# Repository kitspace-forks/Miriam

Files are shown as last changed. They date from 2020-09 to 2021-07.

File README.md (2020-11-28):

Miriam
========



Miriam is an open-source instrument for isothermal amplification reactions such as LAMP and realtime fluorescence detection. The costs per instrument are below 1000 USD, and our goal is to make it less expensive, more robust, and ready for volume production. It could be used as part of a test for Covid-19 😷.

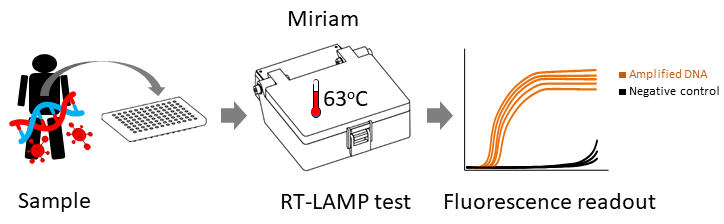
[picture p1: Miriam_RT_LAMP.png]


**🔥 Update 2020 Oct 15 🔥** Updates are coming. We have built and tested a Miriam device and will be updating this repository with details soon. In the meantime, the new [BOM list](PCB/BOM) of the Covid-19 adapted Miriam is updated constantly during our test.

## User guide ##

View the [Miriam User Guide](https://docs.google.com/document/d/1WqGBbrccB8vQHHecIBe8Pv8aZ-rZUhXWWKjNA4fbFT0/edit?usp=sharing) as a Google Doc. Comments and suggestions are welcome.

## Help wanted

Currently, we are seeking help testing and improving the device. If you have skills circuit board layout, product design, software engineering, user interface design,  and thermal simulation, we could use your help. Furthermore, if you would like to collaborate to put this instrument to real world use, please file an issue or contact [Andrew Straw](<straw@bio.uni-freiburg.de>).

## License



Copyright Miroculus Inc.2016
Based on original work from Arduino (Sweden)

This documentation describes Open Hardware and is licensed under the CERN OHL v. 1.2.

Licensed under CERN OHL v.1.2

You may redistribute and modify this documentation under the terms of the [CERN OHL v.1.2.](http://ohwr.org/cernohl). This documentation is distributed WITHOUT ANY EXPRESS OR IMPLIED WARRANTY, INCLUDING OF MERCHANTABILITY, SATISFACTORY QUALITY AND FITNESS FOR A PARTICULAR PURPOSE. Please see the CERN OHL v.1.2 for applicable conditions

## Introduction

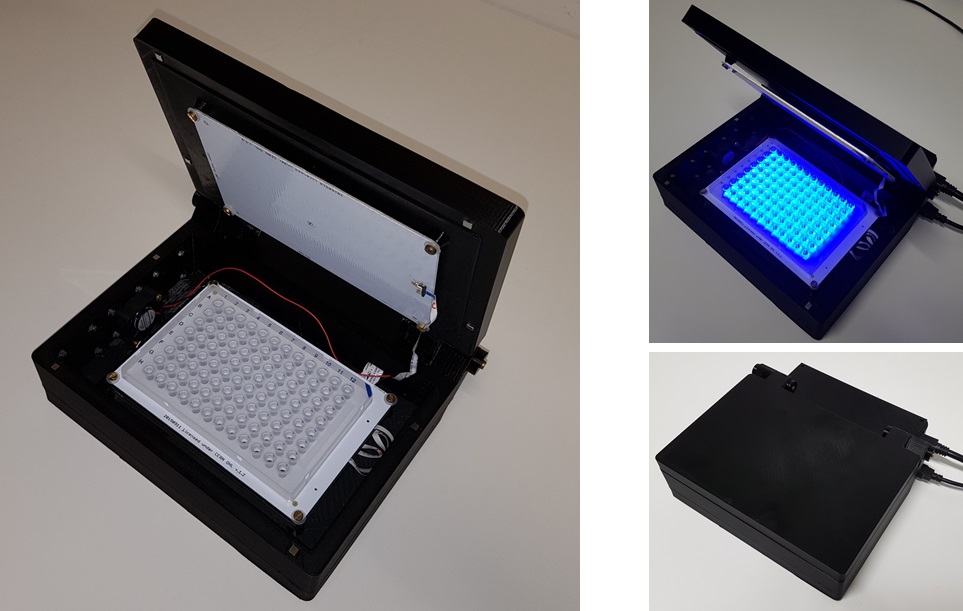
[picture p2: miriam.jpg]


Miriam is optimized for the Syto 9 fluorescent intercalating DNA dye. (The original design was for [calcein dye](http://loopamp.eiken.co.jp/e/products/fluore/index.html). The selected LED is an angle SMD led with peak wavelength 461nm. The photodiode is an RGB photodiode most sensitive to green light. The optics also include an emission filter utilized in theatrical lighting.  The development and selection of components is further described in a [Master's thesis](http://lutpub.lut.fi/handle/10024/159386) done from miriam. 

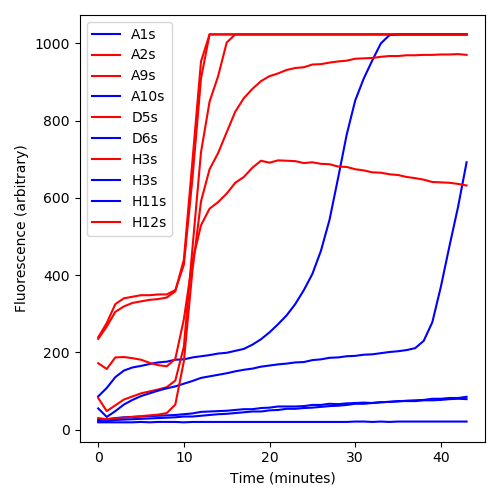
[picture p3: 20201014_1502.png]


**Figure 1.** LAMP reaction in 96 well plate. The reaction was performed in the center and corners of the 96 well plate to test heat uniformity.

In the performance testing of Miriam, the detection limit for DNA using LAMP as amplification platform has been 2amol in 10ul of sample (figure 1).



**Figure 2.** LAMP reaction with 2amol DNA input, fluorescence measured every 2 minutes (y, Normalized signal and x, cycle (2 min).

To report an issue, go to the [issues](http://github.com/strawlab/Miriam/issues) section

If you're interested in modifying or extending the Miriam platform, we strongly suggest you to send us an email discussing your ideas. That way you can coordinate with our team and others, giving your work a higher chance of being integrated into the official release.

## Design

The optics of Miriam plus are designed to support Syto9 + DNA. The emission and absorption spectra of Syto9 + DNA are represented in Figure 3.

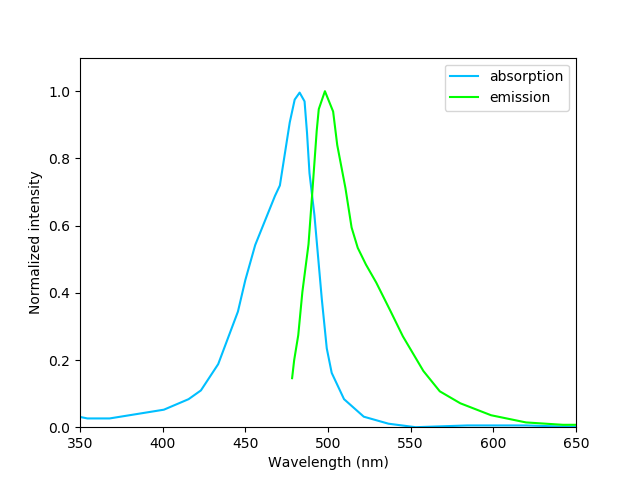
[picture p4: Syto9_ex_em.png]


**Figure 3.** Syto9+DNA emission and excitation spectra.

LEE filter 738 is used for blocking the excitation light. Whole optic design of Miriam plus is shown in Figure 4.

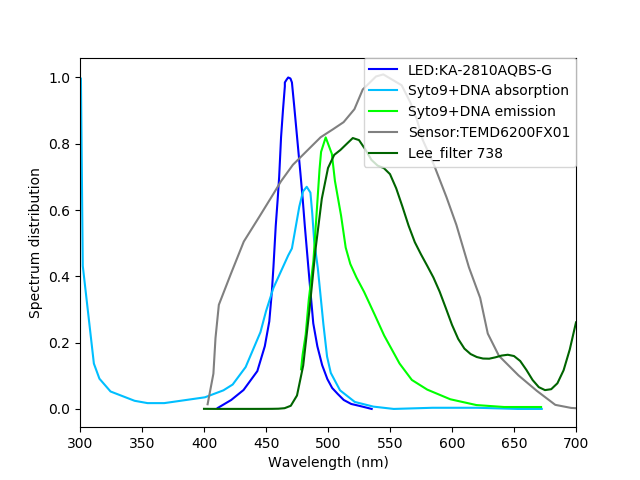
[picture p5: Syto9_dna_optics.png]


**Figure 4.** Optic design for Miriam plus to detect Syto9 + DNA.

The middle heating board and the LED and PD arrangements have been designed to support 96-well plates with the following dimensions (figure 5).



**Figure 5.** 96-well plate dimensions supported by Miriam

To control the heating of Miriam there are two heater PCBs. They have been designed so that in the middle is a 10 kohm SMD thermistor and the heat is generated by current flowing through the copper traces. These traces have been designed to be so long and narrow that they create an internal resistance of few ohms. The traces are closer to each other in the edges because heat is measured from the middle and the edges of the PCB boards meet ambient air and they need to produce more heat. (Figure 6.)

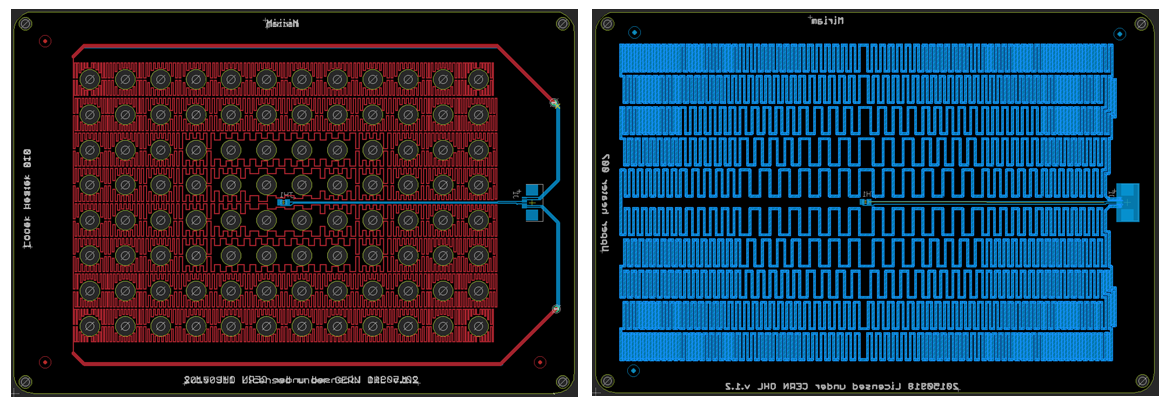
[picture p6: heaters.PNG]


**Figure 6.** Heating plates, heat is generated by trace resistance. Right: The middle heater creating the temperature required for amplification (58-68 degrees C). Left: The top heater keeping vapor from condensing to the lid, kept at 80 degrees C. 

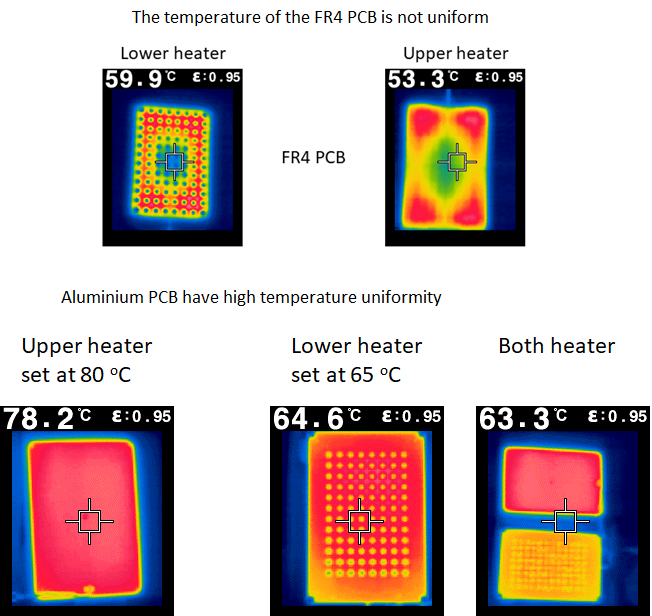
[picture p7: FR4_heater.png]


**Figure 6a.** The distribution of heat in the FR4 and Al heaters. FR4 heaters may work with small number of wells setup. For Miriam, we recommend using Al boards for better heat distribution.

Original Miriam design has 2.5 oC difference in temperature of the central wells and those on the far edge. Adding a heating wire on the edge of the lower heater can improve the uniformity (Fig. 6b). The temperature difference is reduced as low as 1oC or +/-0.5 oC by tuning the heat wire temperature (current) manually. An additional close-loop control for the heating wire would further improve the temperature uniformity.    
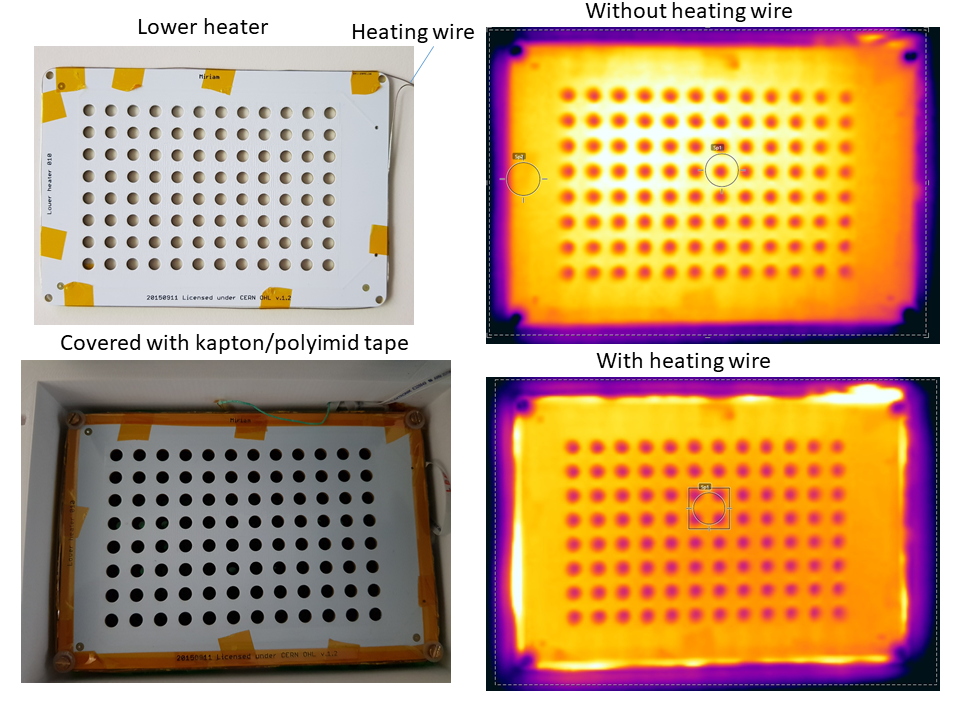
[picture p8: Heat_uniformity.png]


**Figure 6b.** Additional heat wire (left) helps to improve heat uniformity of the plate as in thermography images(right).

The heat uniformity of Miriam would be improved further by optimizing the heating traces of the heaters. Using a PCB thermal analysis software (Fig. 6C) with certain protocol for heat trace optimization would help to boost the design process.

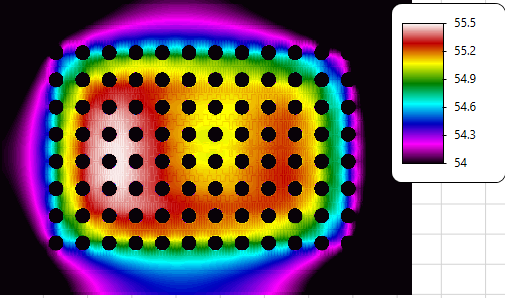
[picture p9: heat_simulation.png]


**Figure 6c.** Heat distribution of the lower heater obtained from PCB thermal analysis software [(More detail of the analysis)](https://www.adam-research.de/en/2020/10/corona-forschung-mit-trm3/).

The detection of fluorescence is done with 96 LEDs and 96 photodiodes creating LED and photodiode PCBs. The LED peak wavelength is 470 nm and photodiode is a green RGB photodiode. The measured voltage is amplified with an operational amplifier to 0-5 V that is then converted by Arduino’s 8-bit ADC to be a numerical value. (figure 7.)

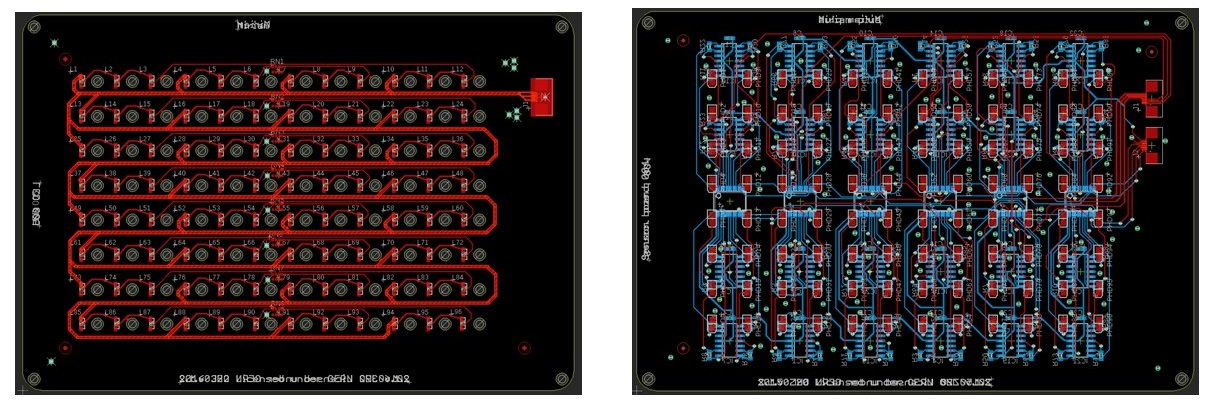
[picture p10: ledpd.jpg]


**Figure 7.** LED (left) and new photodiode (right) PCBs.

All of these boards are controlled by a shield that is directly mounted to the Arduino mega board (figure 8). The shield contains three MOSFETs to control LED board and the two heater boards, the required components to read the heat from the thermistors as well as a WIFI chip. The WIFI chip makes it possible for Arduino to be connected to a local WIFI and this way communicate autonomously to a web service.

shield

**Figure 8.** The Arduino shield. 

Assembly
------------
3D print the printable parts under folder ["3D model"](3D%20Model), sand them if nescessary to make them align with each other. Assemble the boards as presented in the Figure 9. In the assembly cut with scissors the emission filter and glue to the filter holder.

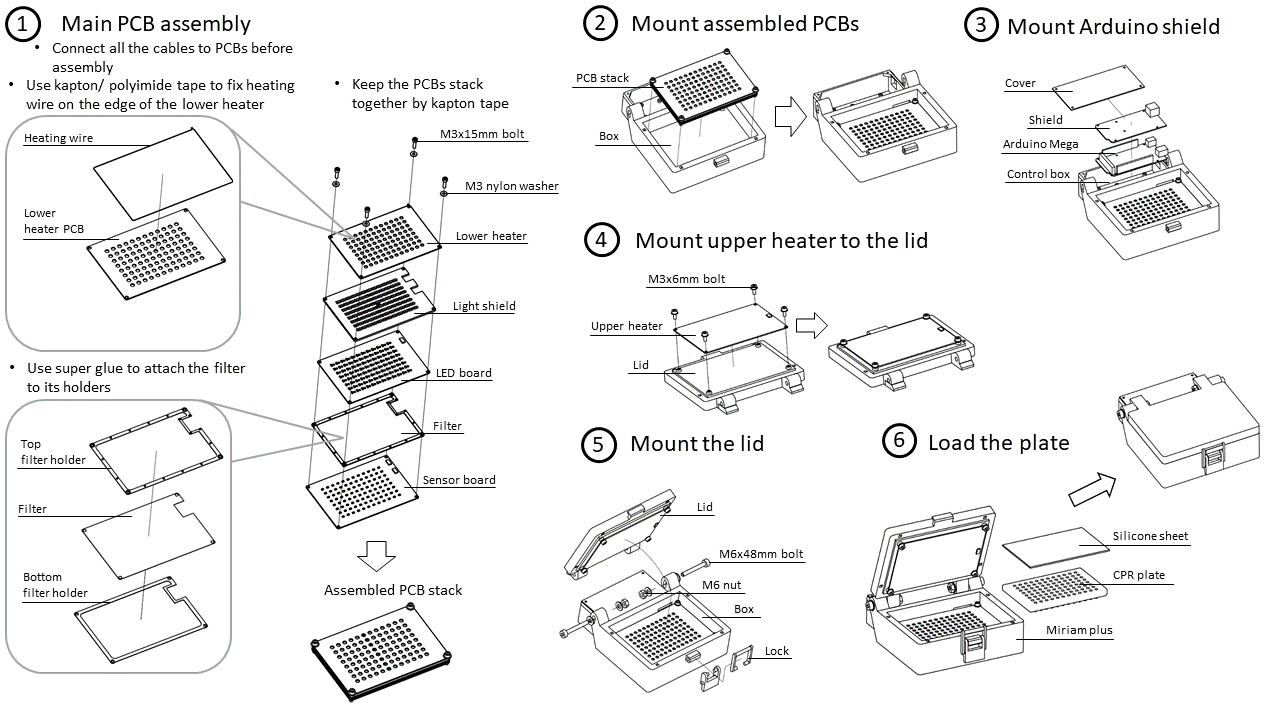
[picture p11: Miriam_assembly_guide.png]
screws


**Figure 9.** Miriam assembly instruction. [High resolution version for printing](Miriam_assembly_guide.pdf) and [Video](https://youtu.be/ynIIGh6IMBA)

**Note:** All the cables used for Miriam must be "Opposite Side Contacts".
          For hand soldering, it is recommended to use solder paste and stencils for the sensor board. If it is possible, use reflow oven for the bottom side.
          
**Updated components:** The new [BOM list](PCB/BOM) of the Covid-19 adapted Miriam will be updated constantly during our test.

Software
------------
We just tested and improved the serial version of the software [Serial_003](Programs/Serial_003).

Improvement wish list
------------
A more robust type of connector can be considered. May change to 1mm pitch. 
Optimization for the traces of lower heater board to have uniformity heat distribution.

Credits
--------
The original Miriam is an open source project, supported by Miroculus in collaboration with Arduino (Sweden). The team was led by Juho Terrijarvi.

This version of Miriam has been improved by [Straw Lab](https://strawlab.org) to make it work with Syto-9 + DNA for potentially Covid-19 test.
Icon and image designed by Miroculus.

The PCB thermal analysis is performed by [ADAM research](https://www.adam-research.de/en/). 

Code of conduct
--------
Anyone who interacts with this software in any space, including but not limited
to this GitHub repository, must follow our [code of
conduct](code_of_conduct.md).

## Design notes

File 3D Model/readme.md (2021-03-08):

# 3D printable parts

Miriam box is composed of 3D printed parts. It is designed to fit the bed of Prusa i3 mk3 printer.
Printer setting is: PETG with 20% cubic infill, 200% speed.

**Attention!!!** If you need to use melting curve, please use ABS for printing the box.

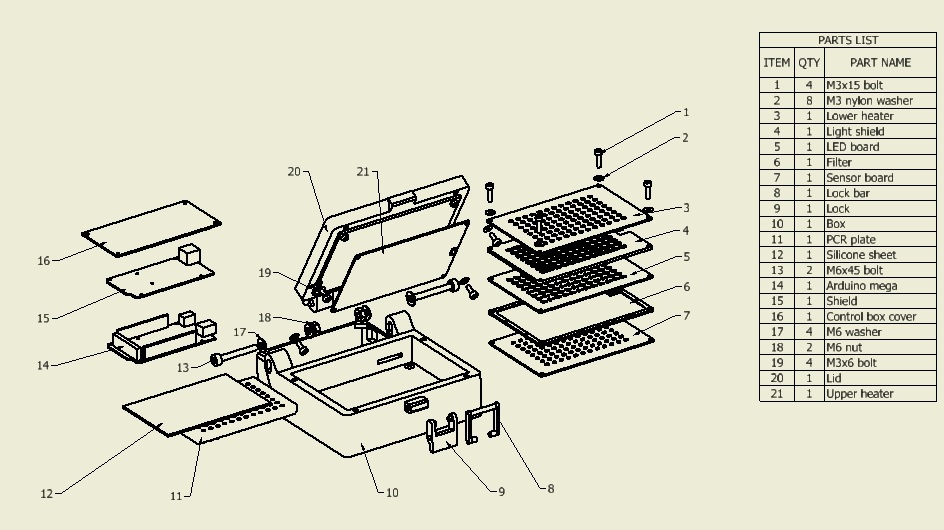
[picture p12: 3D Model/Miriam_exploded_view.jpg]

Exploded view with part list of Miriam. [High resolution version for printing](Miriam_exploded_view.pdf)

## [box.stl](box.stl)

Box is where the mid heating and optic PCBs are located and where the plate to run the assay comes to. It also houses the Arduino Mega and its control shield in the back of the case. 

The outer dimensions of the base are 203 x 173 x 49 mm.

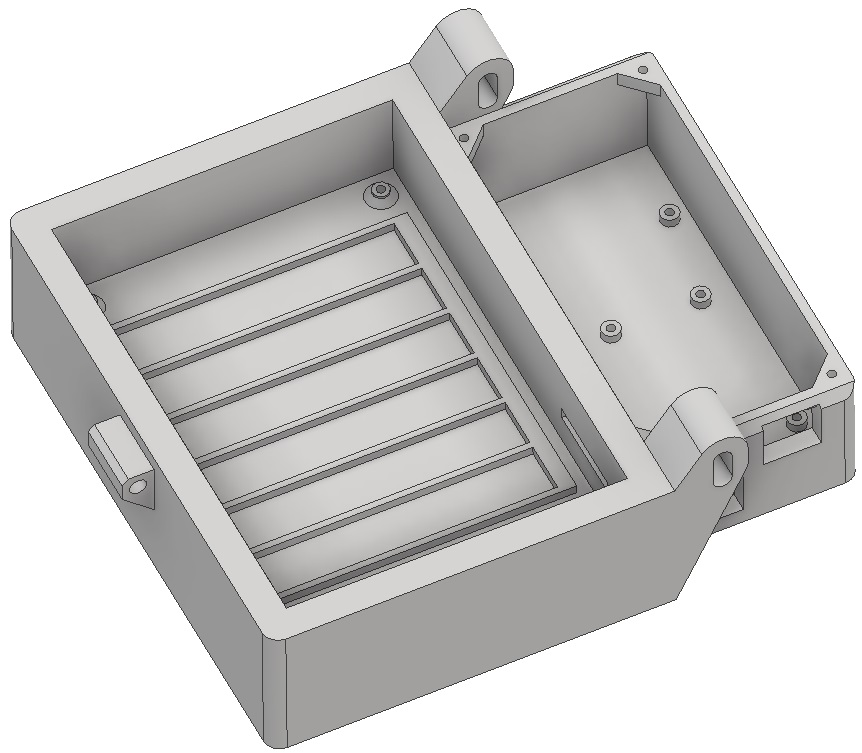
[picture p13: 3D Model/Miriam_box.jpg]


## [lid.stl](lid.stl)

This lid is meant to cover the box and house the upper heating board. The outer dimensions are 165 x 173 x 21 mm.

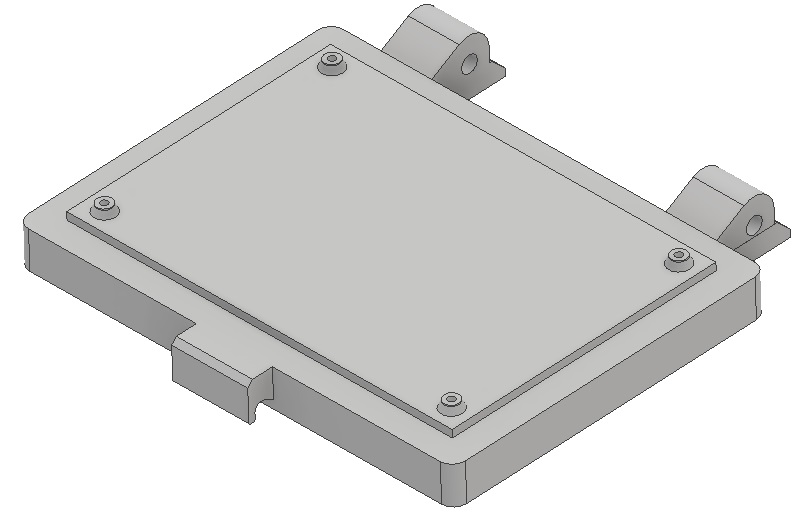
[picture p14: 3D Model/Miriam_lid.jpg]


## [control_cover.stl](control_cover.stl)

Cover is meant to hide the Arduino mega and shield in the back of the case. 

## [filter_holder_bottom.stl](filter_holder_bottom.stl) and [filter_holder_top.stl](filter_holder_top.stl)

Cut the filter and glue it in the middle of these two filters. The bottom one is toward the sensor board.

## [lock.stl](lock.stl) and [lock_bar_new.stl](lock_bar_new.stl)

The lock is meant to tighten the lid during testing.

## [pw_stop_2mm.stl](pw_stop_2mm.stl)

The stopper for the power plug to avoid it to go all the way

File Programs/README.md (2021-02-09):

Miriam SW/FW
========

(c) 2016 Juho Terrijarvi juho@miroculus.com, Miroculus Inc.

(c) 2014 Juanjo Tara j.tara@arduino.cc, Arduino Verkstad AB (For FWs)

These programs are free software: you can redistribute them and/or modify them under the terms of the GNU General Public License as published by the Free Software Foundation, either version 3 of the License, or (at your option) any later version.

These programs are distributed in the hope that they will be useful, but WITHOUT ANY WARRANTY; without even the implied warranty of MERCHANTABILITY or FITNESS FOR A PARTICULAR PURPOSE.  See the GNU General Public License for more details.

You should have received a copy of the GNU General Public License along with this program.  If not, see <http://www.gnu.org/licenses/>.

## Programs

Firmware is written with [Arduino IDE](https://www.arduino.cc/en/main/software) and the software with Visual Studio 2015 open community using C#.

* Serial_003 is meant for communication between computer and Miriam via USB cable and string messages

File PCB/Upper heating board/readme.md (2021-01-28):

# UH_007

- 1 layer PCB
- One sided assembly
- material Aluminium
- 1oz copper
- 1.6 mm thick
- Leadfree HAL
- Black soldermask
- White silkscreen

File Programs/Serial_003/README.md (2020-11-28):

Serial_003
========

This SW / FW combination is meant for serial communication between a computer and Miriam. Miriam is connected with a USB cable to the controlling computer and messaging between the two happen via string messages over RX/TX protocol.
- SW 'R' (read assay) - FW 'A11,A12,...A1,A2, B11,B12,...,B1,B2, ..., E2'
- SW 'i' (info) - FW 'outputMiddle, outputUpper, temperatureUpper, temperatureMiddle, temperatureUpperC, temperatureMiddleC, outputExtra, temperatureExtra, termperatureBox, temperatureExtraC, temperatureBoxC'
- SW 'U param' (upper wanted temperature, i.e. U 80) - FW 'temperatureUpperSet'
- SW 'M param' (middle wanted temperature, i.e. M 63) - FW 'temperatureMiddleSet'
- SW 'E param' (extra wanted temperature, i.e. E 63) - FW 'temperatureExtraSet'
- SW 'T param' (box temperature threshold, i.e. T 45) - FW 'temperatureBoxThrSet'
- SW 'H' (heat boards) - FW 'Heating boards' 
- SW 'C' (cancel, turn off the heat) - FW 'Cancel'
- SW 'l' (turn on status LED) - FW 'Status LED on'
- SW 'o' (turn off status LED) - FW 'Status LED off'

Once the temperature has been set, the actual temperature needs to be refreshed by clicking 'Ask heat'. The assay, once started, can always be turned off simply by closing the program. The assay results are saved to the desktop in a .csv file.

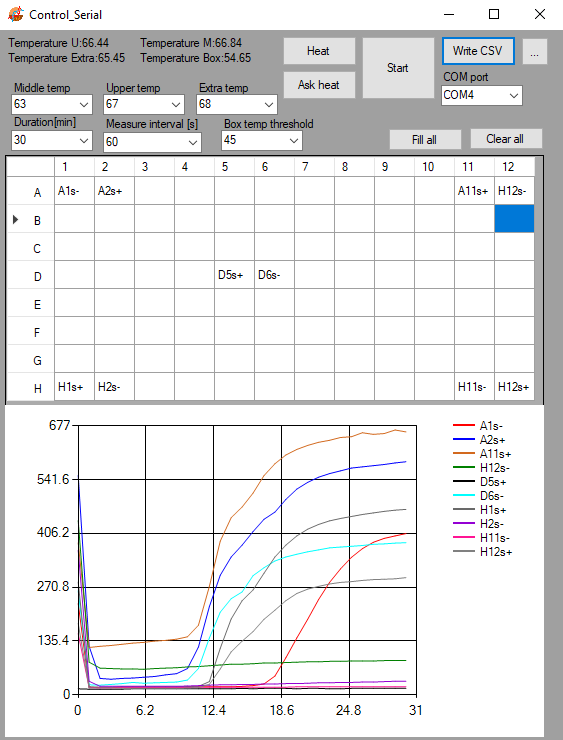
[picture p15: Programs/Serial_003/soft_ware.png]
screws


**Figure 1.** User interface of Serial_003.

Temperature U: measured temperature of the upper heater.

Temperature M: measured temperature of the lower heater.

Temperature Extra: measured temperature of the extra heater (wire).

Temperature Box: measured temperature of the box.

Middle temp: set temperature of the lower heater.

Upper temp: set temperature of the upper heater.

Extra temp: set temperature of the upper heater.

Box threshold: set designed temperature of the box for preheating.

Duration: Total reaction time in minute. After this period, the heaters and sensor readout will stop.

Measure interval: the interval in seconds between two readouts. Minimum value is 11s. For real time measurement, it is recommended to set the interval not lower than 60s as the resistors of the LED board can produce additional heat to the wells in the central collumns. 

COM port: choose your device.

[Heat]: Start heating program.

[Ask heat]: Check the temperature of the heaters and update on the UI.

[Start]: Start the readout cycle as defined by "Duration" and "Measure interval".

[Write CSV]: Save data to CSV.

[...]: Choose folder for saving data.

[Fill all]: Auto name the wells as their positions.

[Clear all]: clear the well name.

**Note:**

The program saves the temperature of the heaters and sensor readouts of all the wells but only plot on the UI those with name filled.

It is recommended to preheat the device at the desired temperature for 30 min before loading the samples.

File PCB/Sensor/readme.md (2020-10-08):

# Sensor_004
- Changed the order of power pins of the connector and the new footprint for new photodiode (TEMD6200FX01)

- material FR4
- 2 layer
- double sided assembly
- 1oz copper
- 1.6 mm thick
- Leadfree HAL
- Black soldermask
- White silkscreen

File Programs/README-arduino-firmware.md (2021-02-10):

# Arduino firmware for Miriam

This requires the [Arduino software](https://www.arduino.cc/en/Guide/Windows).

* `Serial_003` - this contains the source code ("sketch") for the Arduino
  firmware in the file `Serial_003.ino`.
* `PID_v1.zip` - this is a library for Arduino.

## Installing

1. The `PID_v1` library should be installed in the Arduino IDE [according to
   these instructions](https://www.arduino.cc/en/guide/libraries). Follow the
   "Importing a .zip Library" section and select `PID_v1.zip`.

2. In the Arduino IDE, go to "Tools > Board" then select `Arduino Mega or Mega
   2560`.

3. In the Arduino IDE, select the port to the Arduino device. Go to "Tools >
   Port" then select the correct port, which depends on your computer.

4. Then the sketch can then be uploaded using the IDE. [Here is a tutorial about
   getting started with Arduino](https://www.arduino.cc/en/main/howto).

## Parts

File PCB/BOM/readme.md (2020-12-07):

# Components

Components required for the PCB assembly are listed in the BOM files in this
directory. Each .xlsx file contains link to the individual components.

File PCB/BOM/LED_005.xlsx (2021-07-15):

PCB: | LED_003
References | pcs/pcb | Value | Package | Description | Remark | Link
RN1,RN2,RN3,RN4,RN5,RN6,RN7,RN8 | 8 | 181 | CAY16 | Array Chip Resistor | 4R-NCAY16 | https://de.farnell.com/bourns/cat16-181j4lf/widerst-netzwerk-isol-180r-0-063w/dp/2908145
FD1,FD2,FD3 | 3 | FIDUCIALMOUNT | FIDUCIA-MOUNT | FIDUCIALMOUNT
L1,L2,L3,L4,L5,L6,L7,L8,L9,L10,L11,L12,L13,L14,L15,L16,L17,L18,L19,L20,L21,L22,L23,L24,L25,L26,L27,L28,L29,L30,L31,L32,L33,L34,L35,L36,L37,L38,L39,L40,L41,L42,L43,L44,L45,L46,L47,L48,L49,L50,L51,L52,L53,L54,L55,L56,L57,L58,L59,L60,L61,L62,L63,L64,L65,L66,L67,L68,L69,L70,L71,L72,L73,L74,L75,L76,L77,L78,L79,L80,L81,L82,L83,L84,L85,L86,L87,L88,L89,L90,L91,L92,L93,L94,L95,L96 | 96 | KA-2810AQBS-G | LED_0.2 | LED_0.2 | LED | https://de.farnell.com/kingbright/ka-2810aqbs-g/led-smd-2-8x0-8mm-seitl-abstr/dp/2146478
J1 | 1 |  | 68710614522 | WE-FPC 0.5mm SMT ZIF Horizontal Bottom Contact, 6 Pins=>Code : Con_FPC_ZIF_0.50_68710614522 |  | https://de.farnell.com/wurth-elektronik/68710614522/ffc-05mm-90-unten-ziif-6kont/dp/1641913

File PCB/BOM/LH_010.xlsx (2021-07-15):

PCB: | LH_010
References | pcs/pcb | Value | Package | Description | Remark | Link
J1 | 1 |  | 68710614522 | WE-FPC 0.5mm SMT ZIF Horizontal Bottom Contact, 6 Pins=>Code : Con_FPC_ZIF_0.50_68710614522 |  | https://de.farnell.com/wurth-elektronik/68710614522/ffc-05mm-90-unten-ziif-6kont/dp/1641913
TH1 | 1 | 10K | THERMISTOR_SMD_0603 | NTCS0603E3103FLT | NTC | https://www.mouser.de/ProductDetail/594-NTCS0603E3103FLT

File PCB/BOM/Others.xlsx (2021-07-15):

PCB: | UH_007
References | pcs/pcb | Value | Package | Description | Remark | Link
C1, C2 | 2 | 10u | A/3216-18R | POLARIZED CAPACITOR, European symbol |  | https://www.mouser.de/ProductDetail/KEMET/T495A106K010ATA2K0?qs=ds50AKTGxA9fL71AH2RCoQ%3D%3D
TH1, TH2 | 2 | 10K | NTCS0603E3103FLT | THERMISTOR_SMD_0603 | NTC
R1, R2 | 2 | 10k | 0603
Filter | 1 | 738 |  | LEE Filter-Bogen Nr. 738 Jas Green |  | https://www.castinfo.de/produkte/filterfolien/filterfolien/lee-filter-bogen-nr-738-jas-green.html
Power input | 1 | 12V, 10A | ALM120PS12 | External power supply |  | https://de.rs-online.com/web/p/products/1720772/
Thermal Gap Filler Pad | 1 |  | 40001020 |  |  | https://www.mouser.de/ProductDetail/710-40001020
Cable | 5 | 0,5 mm pitch | 687706200002 | opposite side contacts |  | https://www.mouser.de/ProductDetail/710-687706200002
Heating wire |  | RD 100/0,3 |  | Block RD 100/0,3 Widerstandsdraht 6.93 Ω/m 158 m |  | https://www.conrad.de/de/p/block-rd-100-0-3-widerstandsdraht-6-93-m-158-m-422450.html
Arduino Mega 2560 |  |  |  |  |  | https://www.mouser.de/ProductDetail/782-A000067

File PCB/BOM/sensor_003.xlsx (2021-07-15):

PCB: | sensor_002
References | pcs/pcb | Value | Package | Description | Remark | Link
C1,C2,C3,C4,C5,C6,C7,C8,C9,C10,C11,C12,C13,C14,C15,C16,C17,C18,C19,C20,C21,C22,C23,C25 | 24 | 100nF | C0603 | C-EUC0603 | CAPACITOR, European symbol
R1,R2,R3,R4,R5,R7,R8,R9,R10,R11,R12,R13,R14,R15,R16,R17,R18,R19,R20,R21,R22,R23,R24,R25,R26,R27,R28,R29,R30,R31,R32,R33,R34,R35,R36,R37,R38,R39,R40,R41,R42,R43,R44,R45,R46,R47,R48,R49,R50,R51,R52,R53,R54,R55,R56,R57,R58,R59,R60,R61,R62,R63,R64,R65,R66,R67,R68,R69,R70,R71,R72,R73,R74,R75,R76,R77,R78,R79,R80,R81,R82,R83,R84,R85,R86,R87,R88,R89,R90,R91,R92,R93,R94,R95,R96,R97 | 96 | 100Mohm | R0603 | R-EU_R0603 | RESISTOR, European symbol
U1,U2,U3,U4,U5,U6 | 6 | 74HC4067 | SSOP24 | MUX-1X16 | 1x16 Channel Analog Multiplexer/Demultiplexer [Part No.] | https://www.mouser.de/ProductDetail/595-CD74HC4067SM96G4
PHD1,PHD2,PHD3,PHD4,PHD5,PHD6,PHD7,PHD8,PHD9,PHD10,PHD11,PHD12,PHD13,PHD14,PHD15,PHD16,PHD17,PHD18,PHD19,PHD20,PHD21,PHD22,PHD23,PHD24,PHD25,PHD26,PHD27,PHD28,PHD29,PHD30,PHD31,PHD32,PHD33,PHD34,PHD35,PHD36,PHD37,PHD38,PHD39,PHD40,PHD41,PHD42,PHD43,PHD44,PHD45,PHD46,PHD47,PHD48,PHD49,PHD50,PHD51,PHD52,PHD53,PHD54,PHD55,PHD56,PHD57,PHD58,PHD59,PHD60,PHD61,PHD62,PHD63,PHD64,PHD65,PHD66,PHD67,PHD68,PHD69,PHD70,PHD71,PHD72,PHD73,PHD74,PHD75,PHD76,PHD77,PHD78,PHD79,PHD80,PHD81,PHD82,PHD83,PHD84,PHD85,PHD86,PHD87,PHD88,PHD89,PHD90,PHD91,PHD92,PHD93,PHD94,PHD95,PHD96 | 96 | TEMD6200FX01 | PD_0.2 | PD_0.2 | Photodiode | https://www.mouser.de/ProductDetail/782-TEMD6200FX01
FD1,FD2,FD3,FD4,FD5,FD6 | 6 | FIDUCIALMOUNT | FIDUCIALMOUNT | FIDUCIA-MOUNT
IC1,IC2,IC3,IC4,IC5,IC6,IC7,IC8,IC9,IC10,IC11,IC12,IC13,IC14,IC15,IC16,IC17,IC18,IC19,IC20,IC21,IC22,IC23,IC24 | 24 | LMV324 | SO14 |  | OP AMP | https://www.mouser.de/ProductDetail/511-LMV324LIDT
J1, J2 | 2 |  | 68710614522 | WE-FPC 0.5mm SMT ZIF Horizontal Bottom Contact, 6 Pins=>Code : Con_FPC_ZIF_0.50_68710614522 |  | https://de.farnell.com/wurth-elektronik/68710614522/ffc-05mm-90-unten-ziif-6kont/dp/1641913

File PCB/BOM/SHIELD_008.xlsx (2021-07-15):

PCB: | SHIELD_008
References | pcs/pcb | Value | Package | Description | Remark | Link
R7 | 1 | 1.69k | R0603 | RESISTOR, European symbol
R3, R4, R8, R16 | 4 | 100R | R0603 | RESISTOR, European symbol
C2, C5, C7 | 3 | 100n | C0603 | CAPACITOR, European symbol
R1, R2, R5, R6, R9, R13, R14, R15, R17 | 9 | 10K | R0603 | RESISTOR, European symbol
C3, C4 | 2 | 10u | A/3216-18R | POLARIZED CAPACITOR, European symbol |  | https://www.mouser.de/ProductDetail/80-T495A106K10ATA2K0
JP7 | 1 | 10x1F-H8.5 | 1X10 | PIN HEADER
JP5 | 1 | 18x2F-H8.5 | 2X18 | PIN HEADER
J6 | 1 | 22-23-2021 | 22-23-2021 | .100 (2.54mm) Center Header - 2 Pin"
R10 | 1 | 3.3k | R0603 | RESISTOR, European symbol
R11, R12 | 2 | 4.12k | R0603 | RESISTOR, European symbol
C1, PC1, PC2 | 3 | 47u | PANASONIC_D | POLARIZED CAPACITOR, European symbol |  | https://www.mouser.de/ProductDetail/647-UWX0J470MCL1
JP1, JP2, JP3, JP4, JP6 | 5 | 8x1F-H8.5 | 1X08 | PIN HEADER
IC1, IC2, IC3, IC6 | 4 | PSMN017-30BL,118 | PSMN017-30BL,118 | N-Channel PowerTrench MOSFET |  | https://www.mouser.de/ProductDetail/771-PSMN017-30BL%2c118
WIFI | 1 | ESP12 | ESP12 | ESP8266 Wifi module 12 |  | https://www.mouser.de/ProductDetail/485-2491
D1, D2 | 2 | S1AB-13-F | S1AB-13-F | DIODE |  | https://www.mouser.de/ProductDetail/621-S1AB-F
F1 | 1 | MF-R1100 | LITTLEFUSE | LITTLEFUSE |  | https://www.mouser.de/ProductDetail/652-MF-R1100
IC4 | 1 | NCV1117ST50T3GOSCT-ND | SOT223 | Adjustable Output Low Dropout Voltage Regulator 800 mA |  | https://www.mouser.de/ProductDetail/863-NCV1117ST50T3G
IC5 | 1 | NCV1117ST33T3GOSCT-ND |  | Adjustable Output Low Dropout Voltage Regulator 800 mA |  | https://www.mouser.de/ProductDetail/863-NCV1117ST33T3G
D3, D4, D5, D6 | 4 | RGL34G-E3/98 | RGL34G-E3/98 | Semiconductor diode |  | https://de.farnell.com/vishay/rgl34g-e3-98/diode-fast-0-5a-400v-smd/dp/1336528?st=RGL34G-E3/98
J7 | 1 | KPJX-4S-S | KPJX-4S-S | 4 _Power_ Position Circular Connector Jack, Female Sockets Solder |  | https://www.mouser.de/ProductDetail/806-KPJX-4S-S
J1, J2, J3, J4, J5 | 5 |  | 68710614522 | WE-FPC 0.5mm SMT ZIF Horizontal Bottom Contact, 6 Pins=>Code : Con_FPC_ZIF_0.50_68710614522 |  | https://de.farnell.com/wurth-elektronik/68710614522/ffc-05mm-90-unten-ziif-6kont/dp/1641913

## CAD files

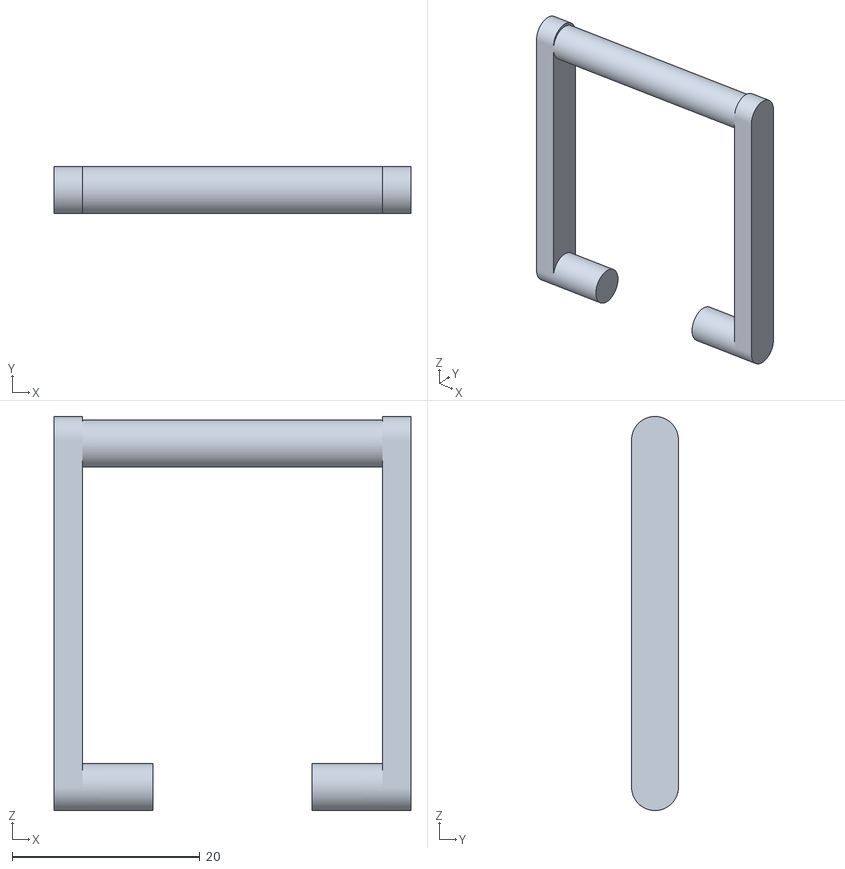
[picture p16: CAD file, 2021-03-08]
3D Model/lock_bar_new.stl
38.0 x 5.00 x 42.0

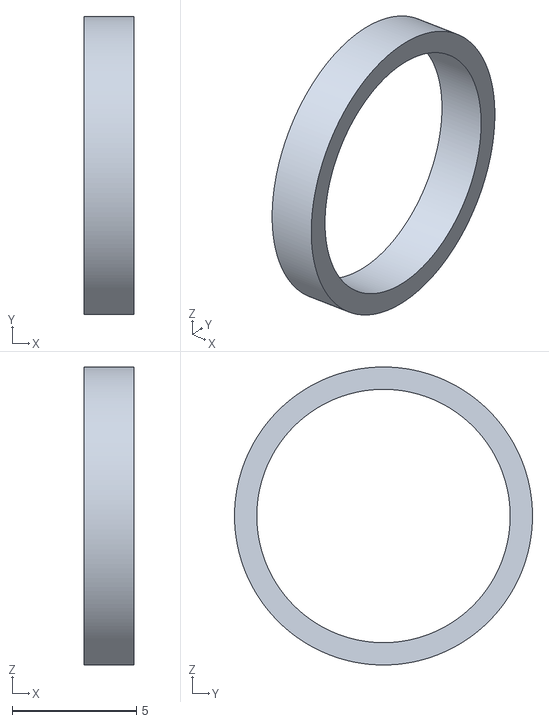
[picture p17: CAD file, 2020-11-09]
3D Model/pw_stop_2mm.stl
2.00 x 12.0 x 12.0

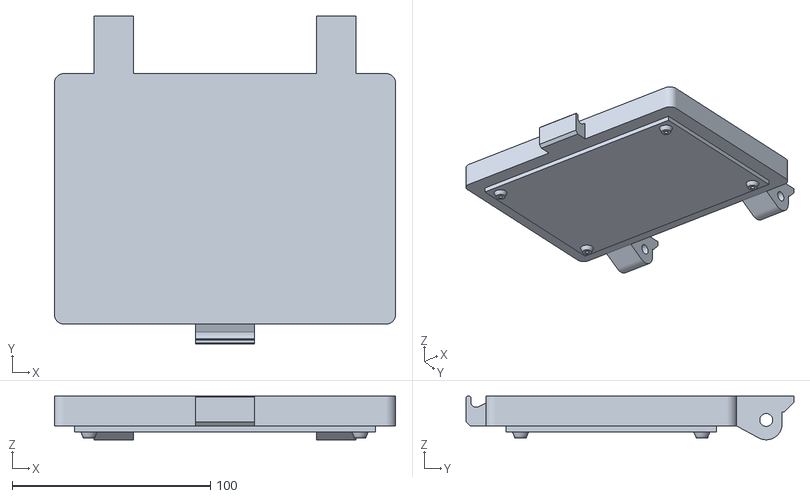
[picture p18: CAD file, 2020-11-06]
3D Model/lid.stl
172.3 x 165.5 x 22.0

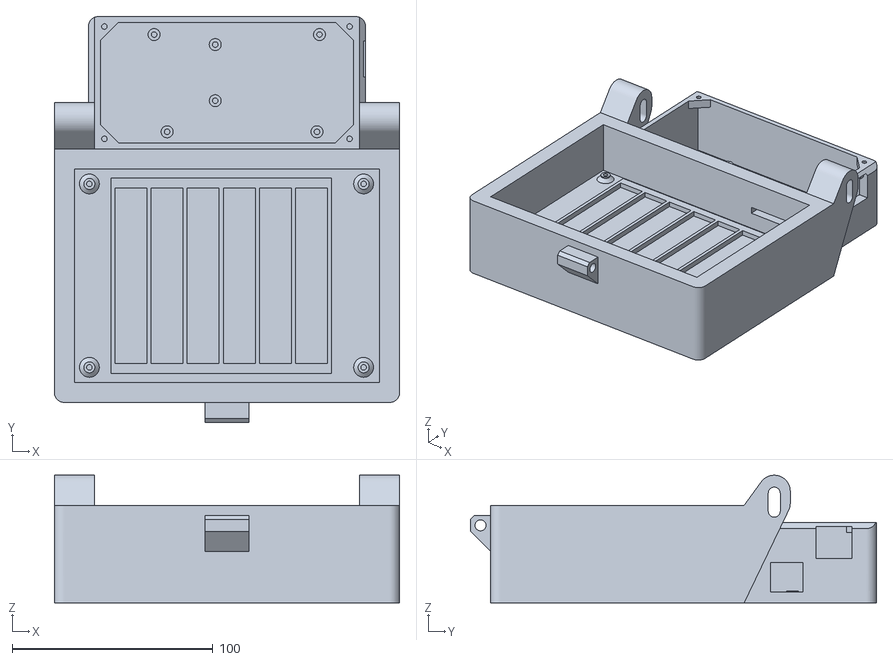
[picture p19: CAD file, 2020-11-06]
3D Model/box.stl
172.3 x 202.5 x 63.6

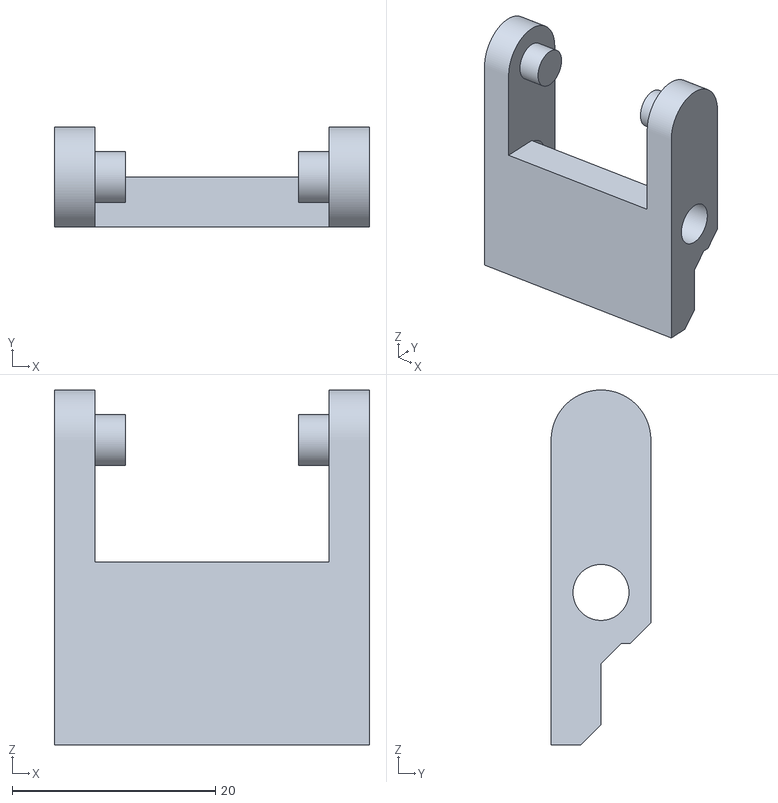
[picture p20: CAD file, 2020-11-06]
3D Model/lock.stl
31.0 x 9.80 x 34.9

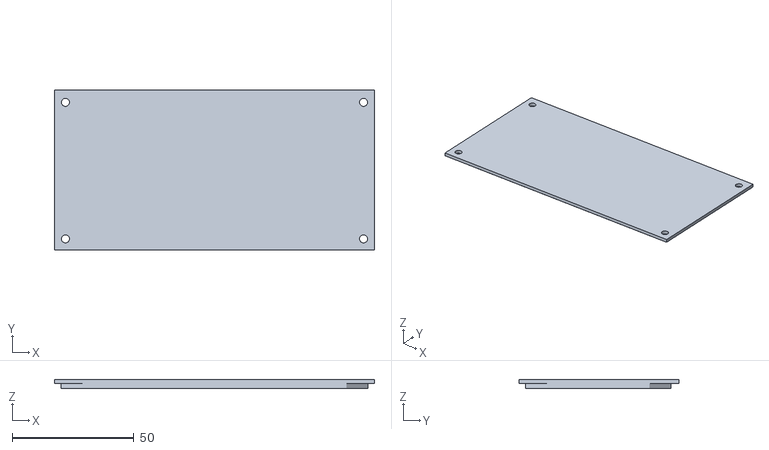
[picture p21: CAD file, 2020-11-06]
3D Model/control_cover.stl
131.3 x 65.5 x 3.50

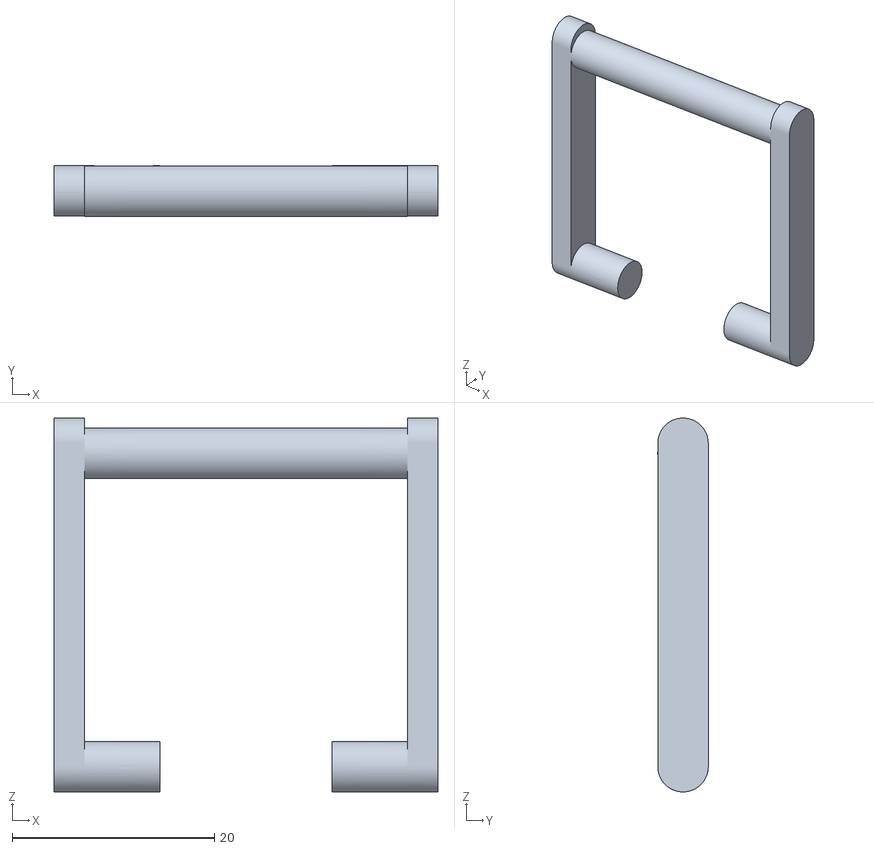
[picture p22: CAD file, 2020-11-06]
3D Model/lock_bar.stl
38.0 x 5.00 x 37.0

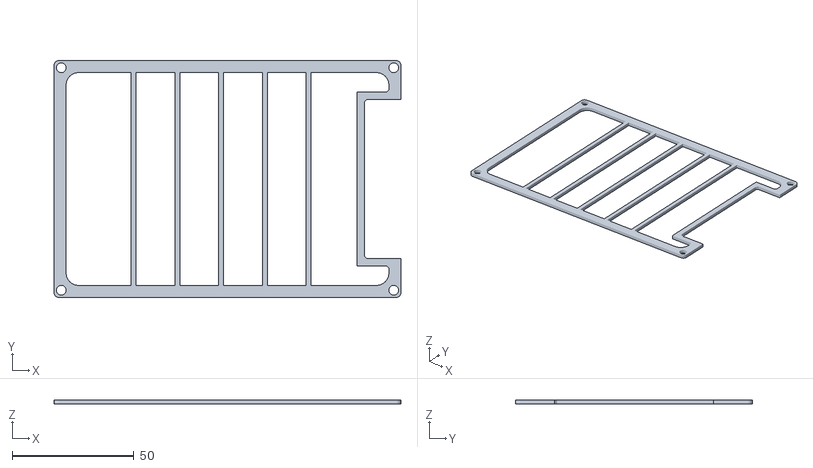
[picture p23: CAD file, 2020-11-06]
3D Model/filter_holder_top.stl
142.8 x 97.5 x 1.80

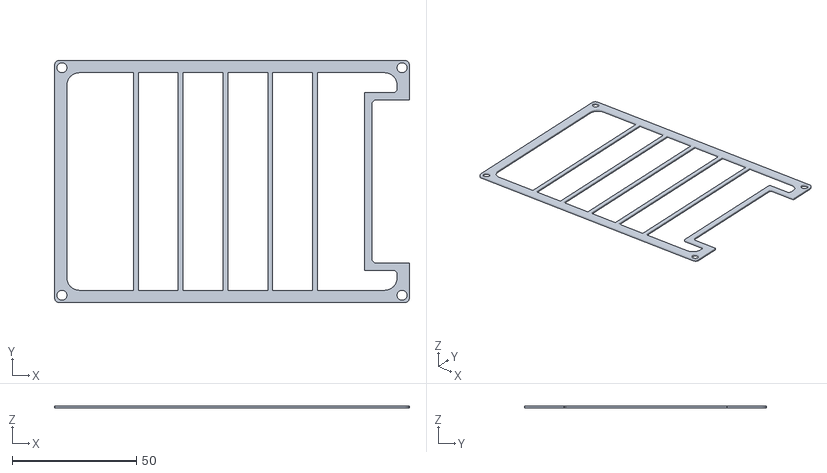
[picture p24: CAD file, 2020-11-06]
3D Model/filter_holder_bottom.stl
142.8 x 97.5 x 1.00

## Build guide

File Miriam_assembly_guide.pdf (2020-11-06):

# 1 Main PCB assembly

# 2 Mount assembled PCBs

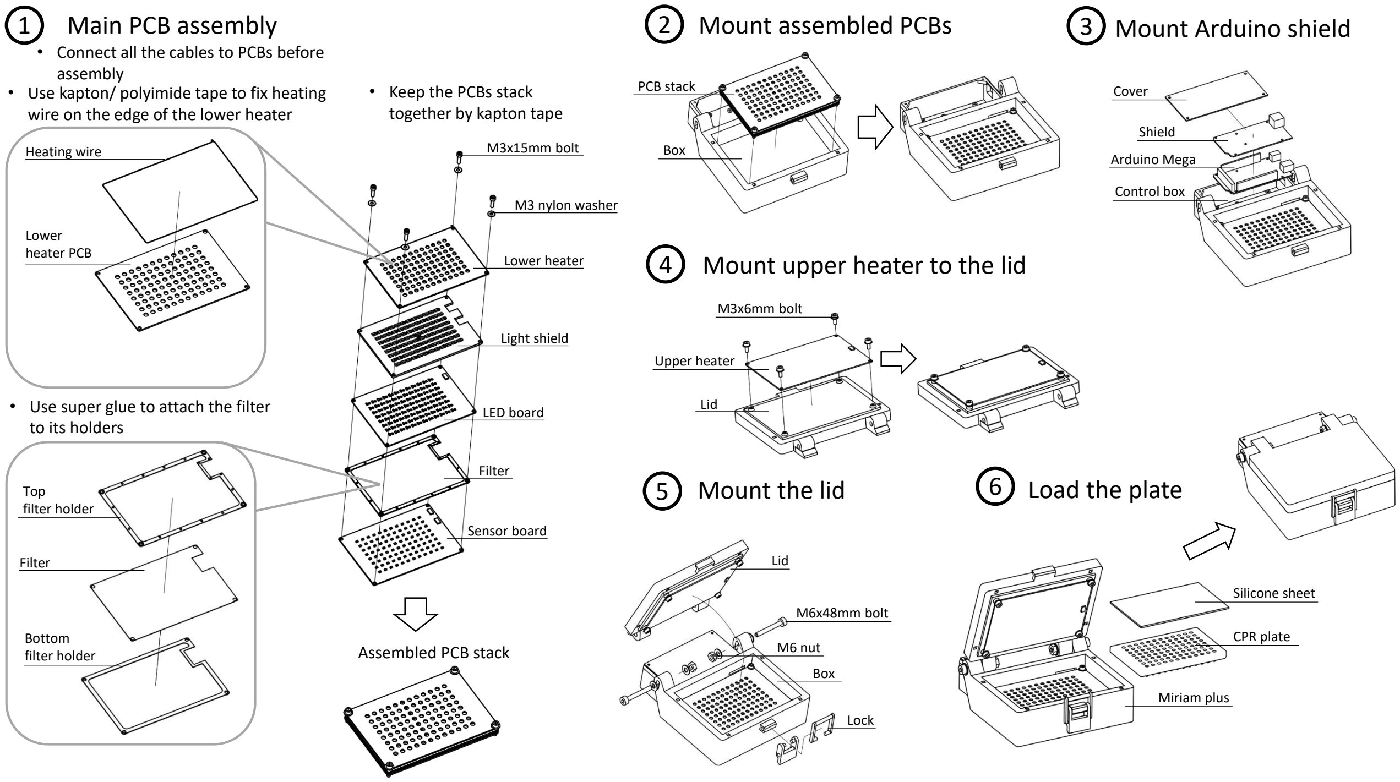
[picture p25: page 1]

Heating wire

### - Keep the PCBs stack together by kapton tape

Lower
heater PCB

Top
filter holder

Filter

Bottom
filter holder

M3x15mm bolt

M3 nylon washer

Lower heater

Light shield

LED board

Filter

Sensor board

### - Use kapton/ polyimide tape to fix heating wire on the edge of the lower heater

### - Use super glue to attach the filter to its holders

### Assembled PCB stack

Box

PCB stack

# 4 Mount upper heater to the lid

Lid

Upper heater

M3x6mm bolt

# 3 Mount Arduino shield

Control box

Arduino Mega

Shield

Cover

# 5 Mount the lid

M6x48mm bolt

Lid

Box

Lock

# 6 Load the plate

Silicone sheet

CPR plate

Miriam plus

### - Connect all the cables to PCBs before assembly

M6 nut

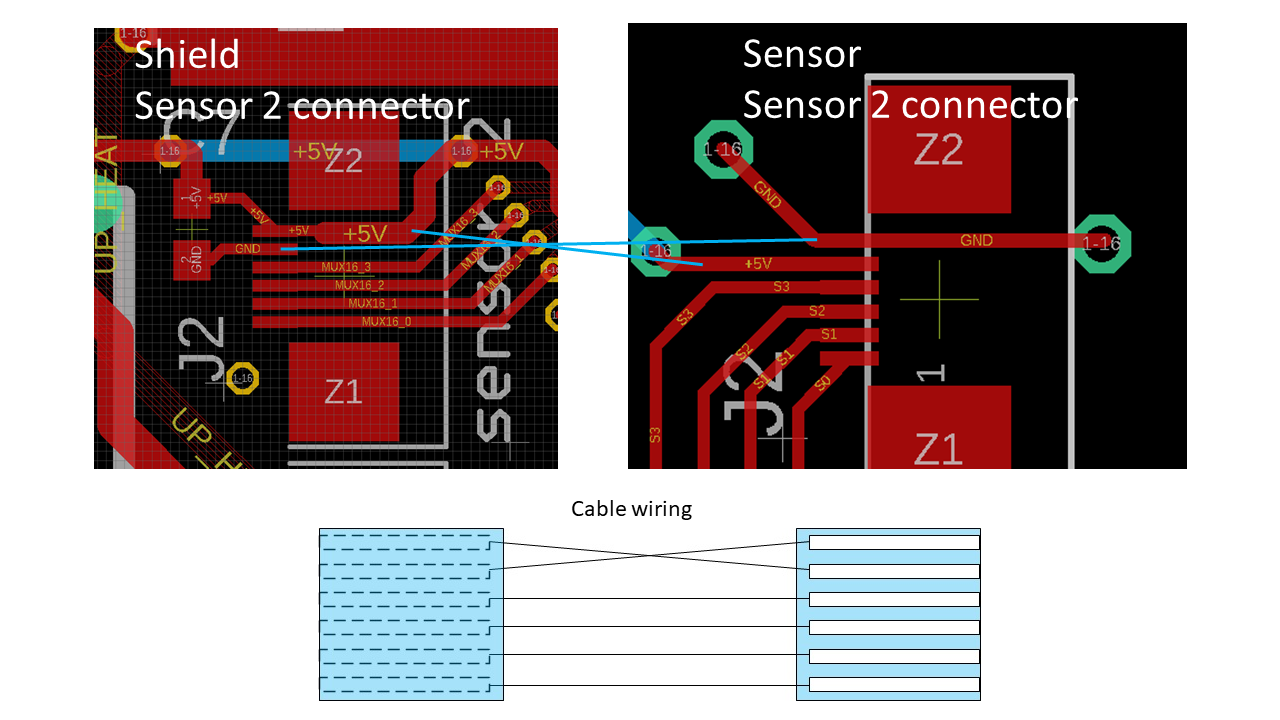
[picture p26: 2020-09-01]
sensor2_wiring.png

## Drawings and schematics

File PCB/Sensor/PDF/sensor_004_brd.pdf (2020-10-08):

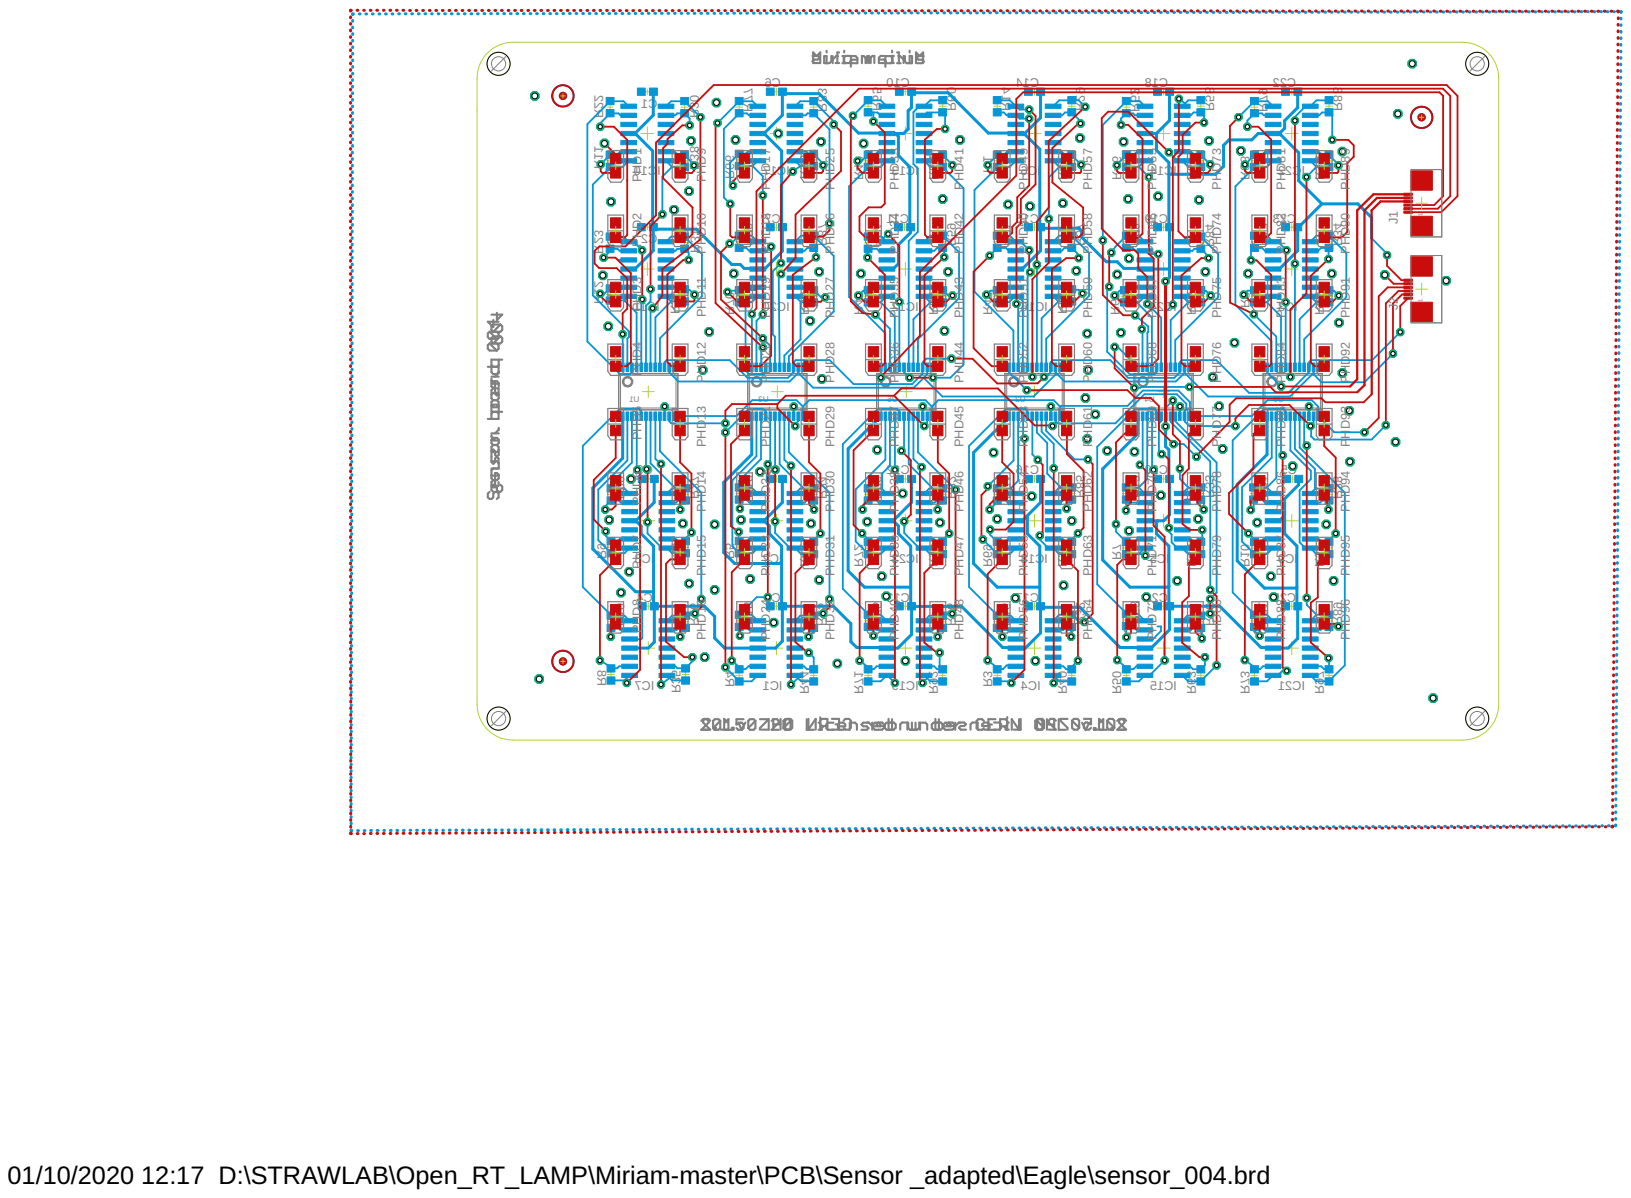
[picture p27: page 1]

01/10/2020 12:17 D:\STRAWLAB\Open_RT_LAMP\Miriam-master\PCB\Sensor _adapted\Eagle\sensor_004.brd

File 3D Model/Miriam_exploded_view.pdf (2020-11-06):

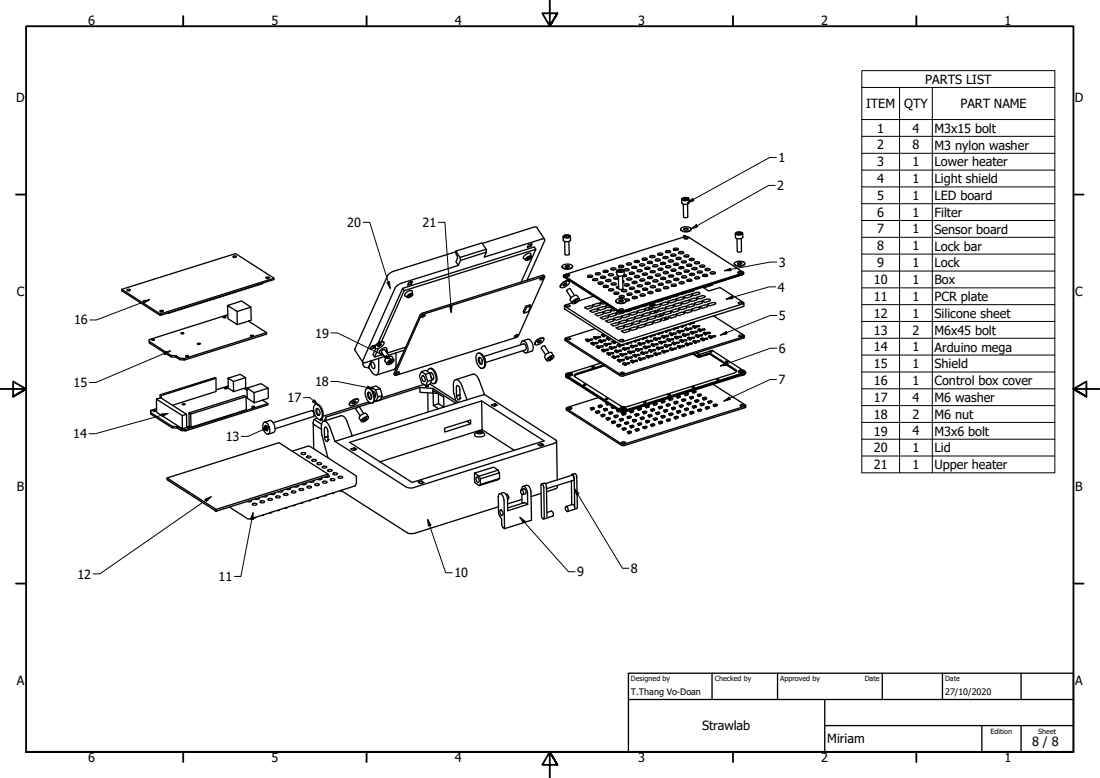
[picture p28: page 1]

1 | 4 | M 3 x 1 5 b olt
2 | 8 | M 3 n ylo n w a s h e r
3 | 1 | L o w e r h e a t e r
4 | 1 | L i g h t s h i eld
5 | 1 | L E D b o a r d
6 | 1 | F ilt e r
7 | 1 | S e n s o r b o a r d
8 | 1 | L o c k b a r
9 | 1 | L o c k
1 0 | 1 | B o x
1 1 | 1 | P C R pla t e
1 2 | 1 | S ili c o n e s h e e t
1 3 | 2 | M 6 x 4 5 b olt
1 4 | 1 | A r d u i n o m e g a
1 5 | 1 | S h i eld
1 6 | 1 | C o n t r ol b o x c o v e r
1 7 | 4 | M 6 w a s h e r
1 8 | 2 | M 6 n u t
1 9 | 4 | M 3 x 6 b olt
2 0 | 1 | L i d
2 1 | 1 | U p p e r h e a t e

S t r a wla b

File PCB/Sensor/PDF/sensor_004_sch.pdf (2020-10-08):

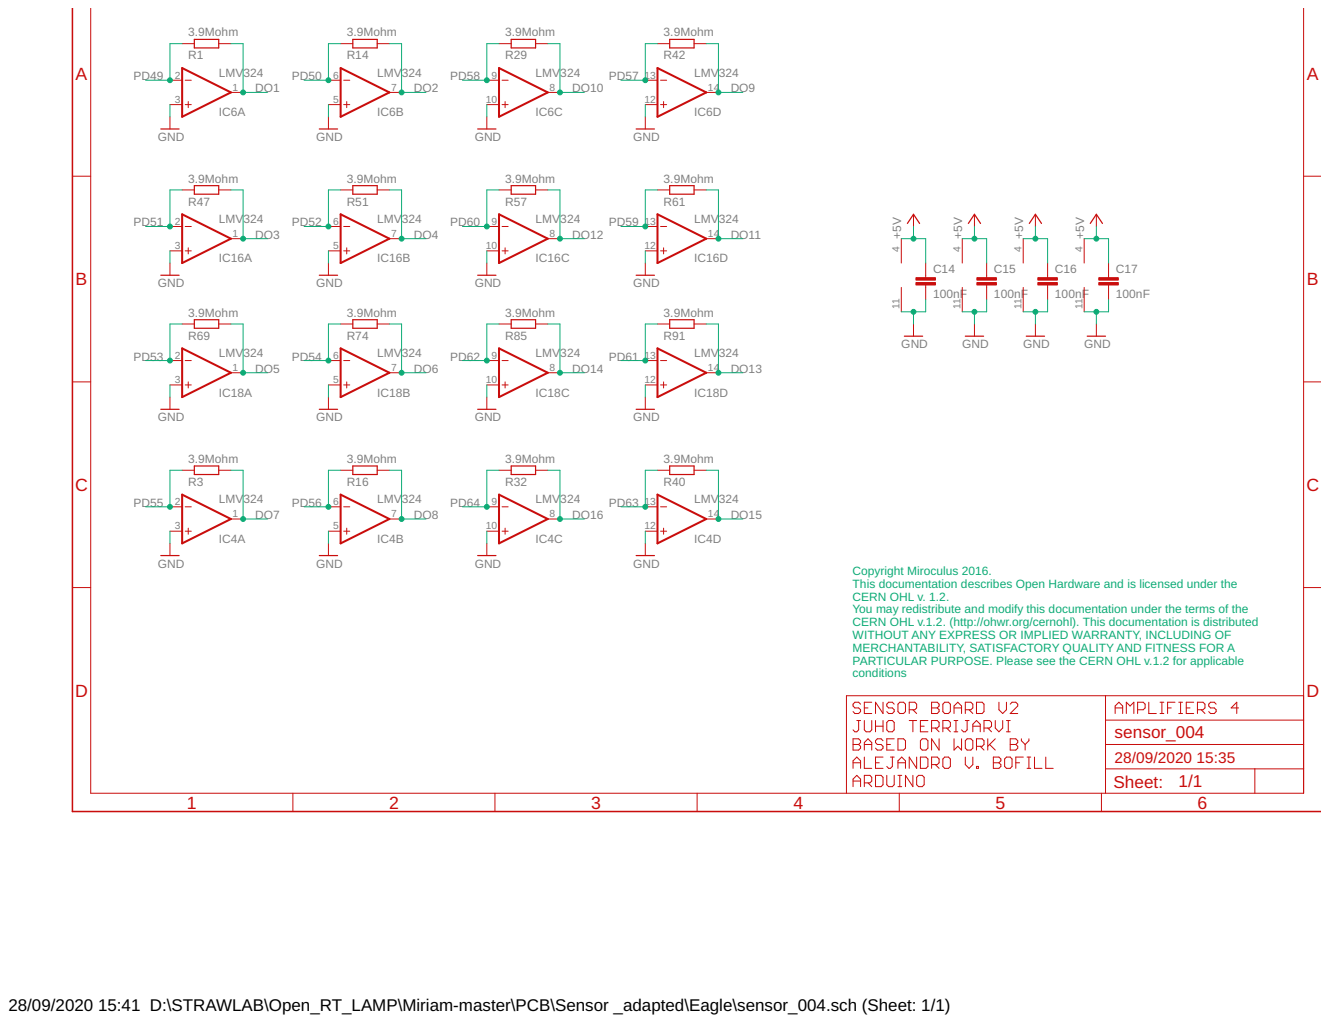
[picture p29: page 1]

Copyright Miroculus 2016. This documentation describes Open Hardware and is licensed under the CERN OHL v. 1.2. You may redistribute and modify this documentation under the terms of the CERN OHL v.1.2. (http://ohwr.org/cernohl). This documentation is distributed

WITHOUT ANY EXPRESS OR IMPLIED WARRANTY, INCLUDING OF
MERCHANTABILITY, SATISFACTORY QUALITY AND FITNESS FOR A
PARTICULAR PURPOSE. Please see the CERN OHL v.1.2 for applicable
conditions

28/09/2020 15:41 D:\STRAWLAB\Open_RT_LAMP\Miriam-master\PCB\Sensor _adapted\Eagle\sensor_004.sch (Sheet: 1/1)

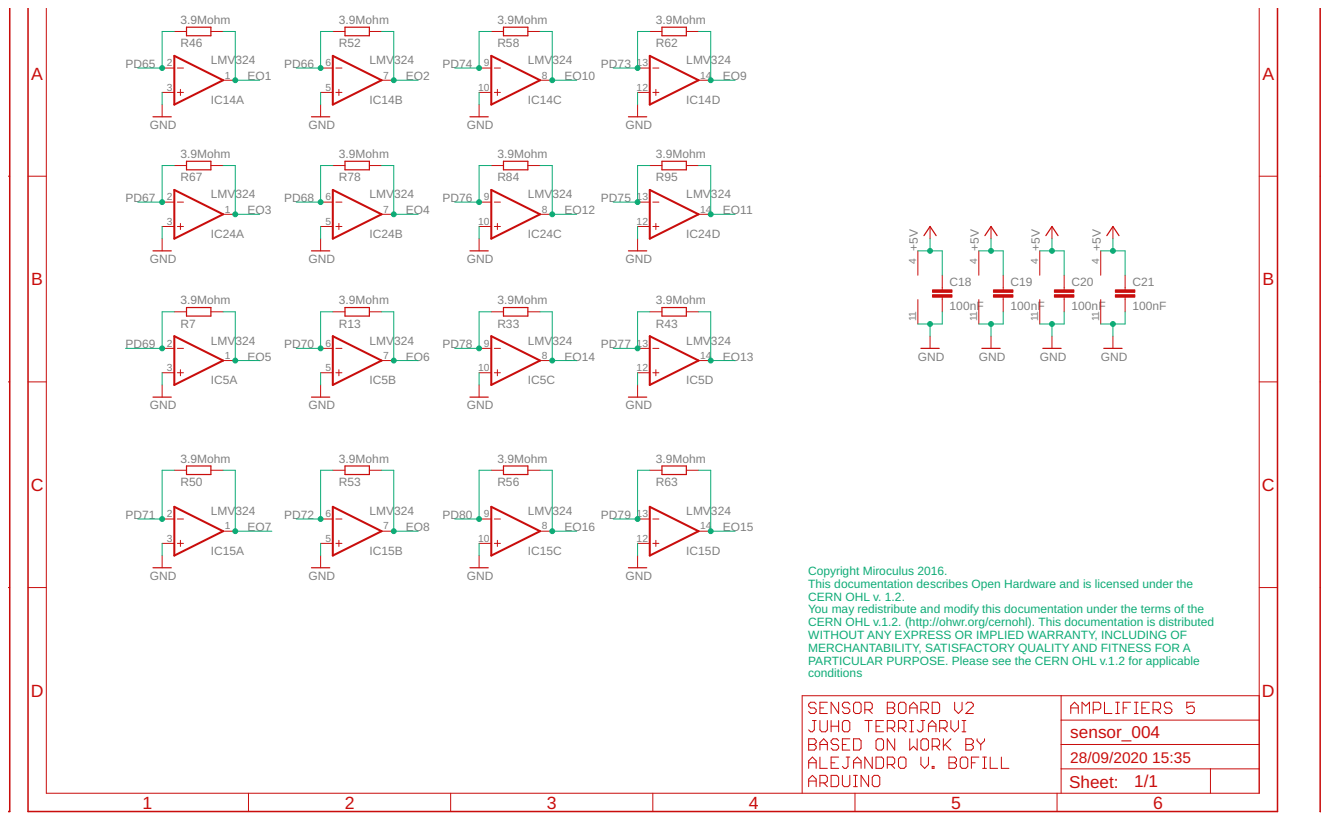
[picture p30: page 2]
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

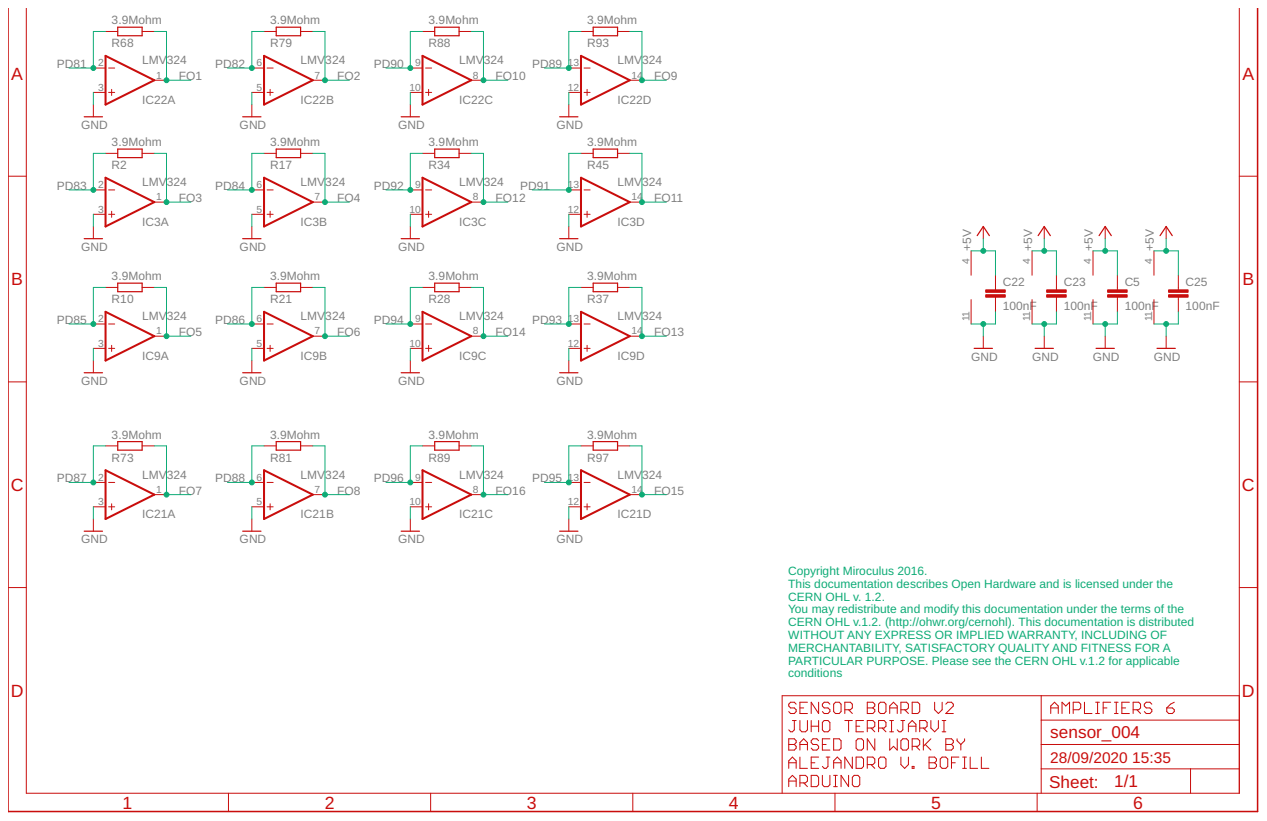
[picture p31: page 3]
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

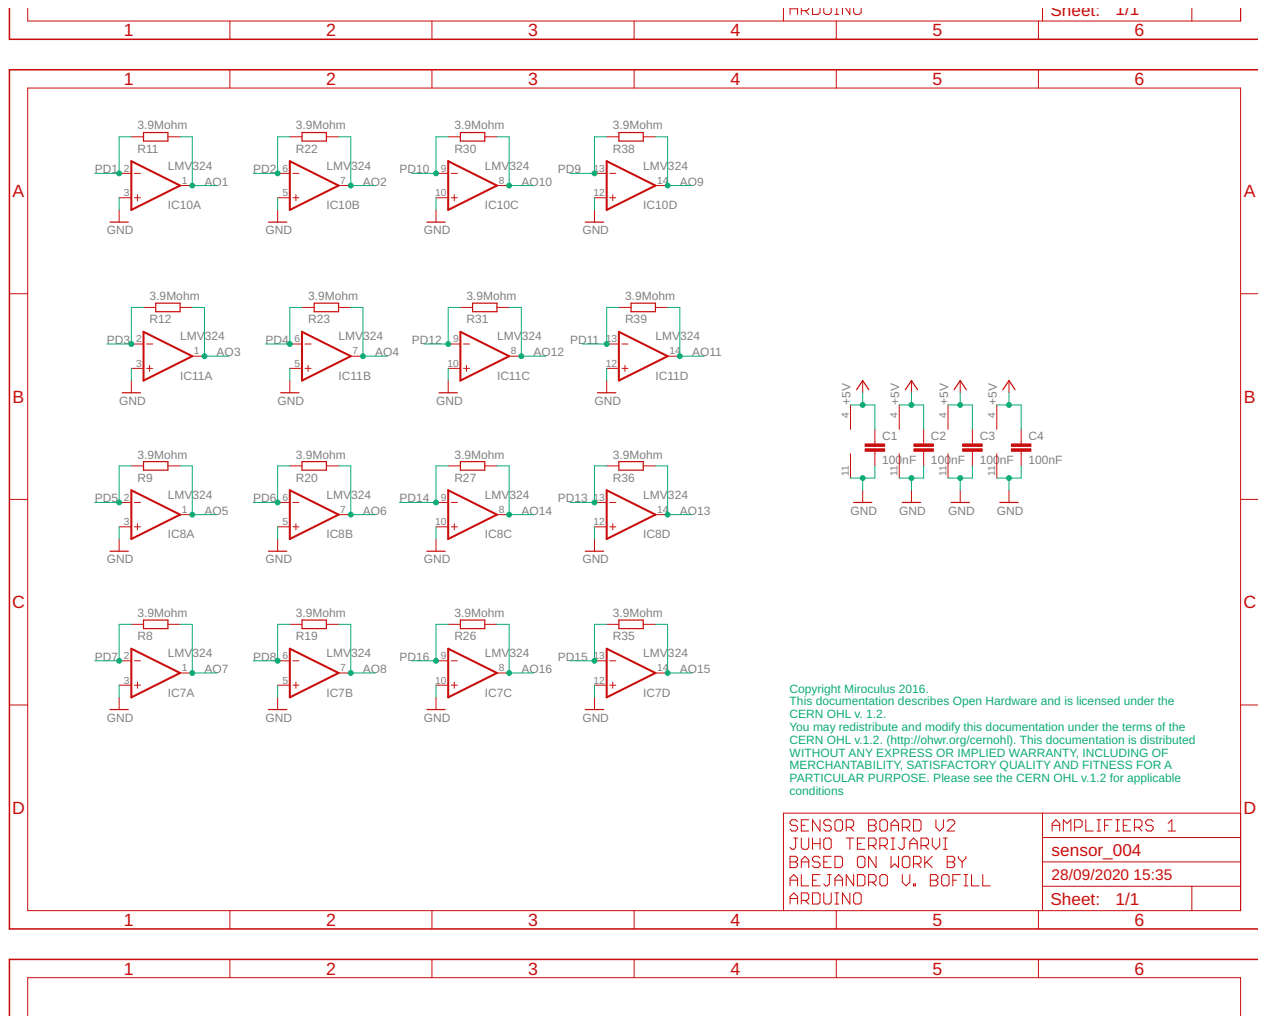
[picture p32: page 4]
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

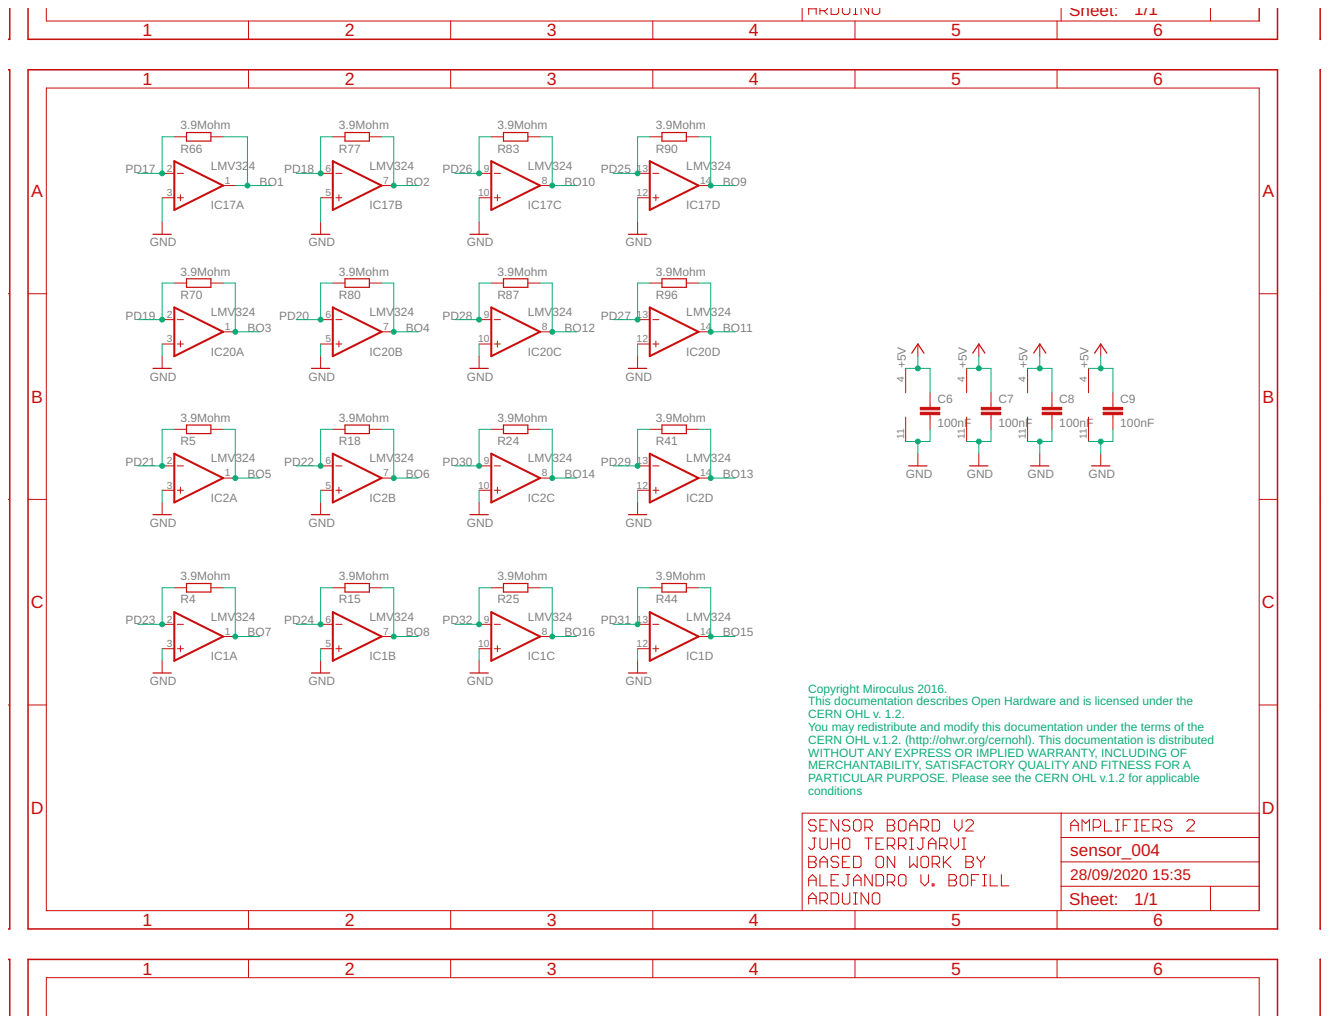
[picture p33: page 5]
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

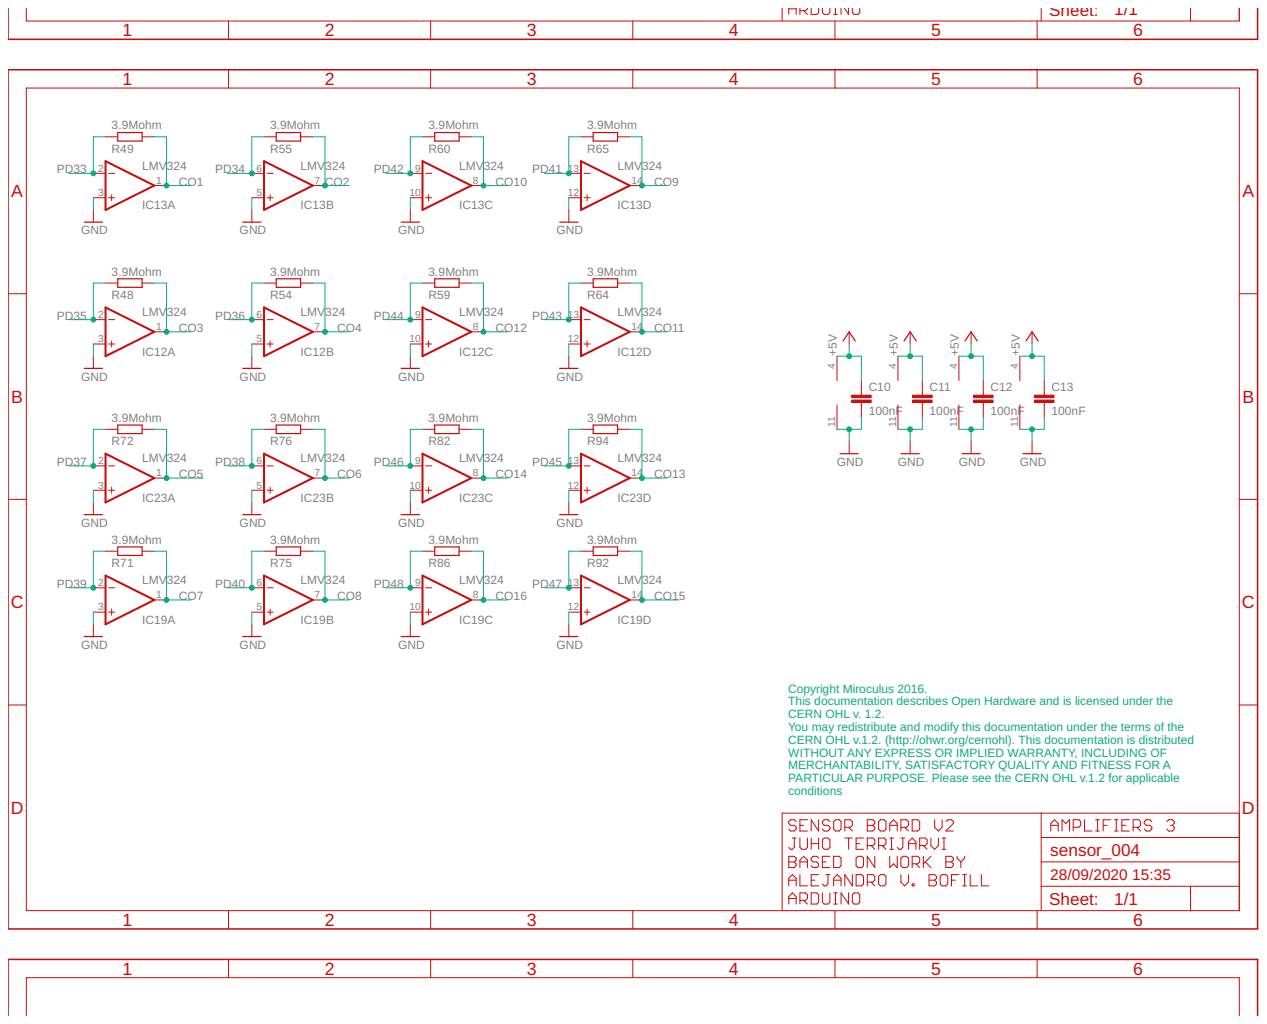
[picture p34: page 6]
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

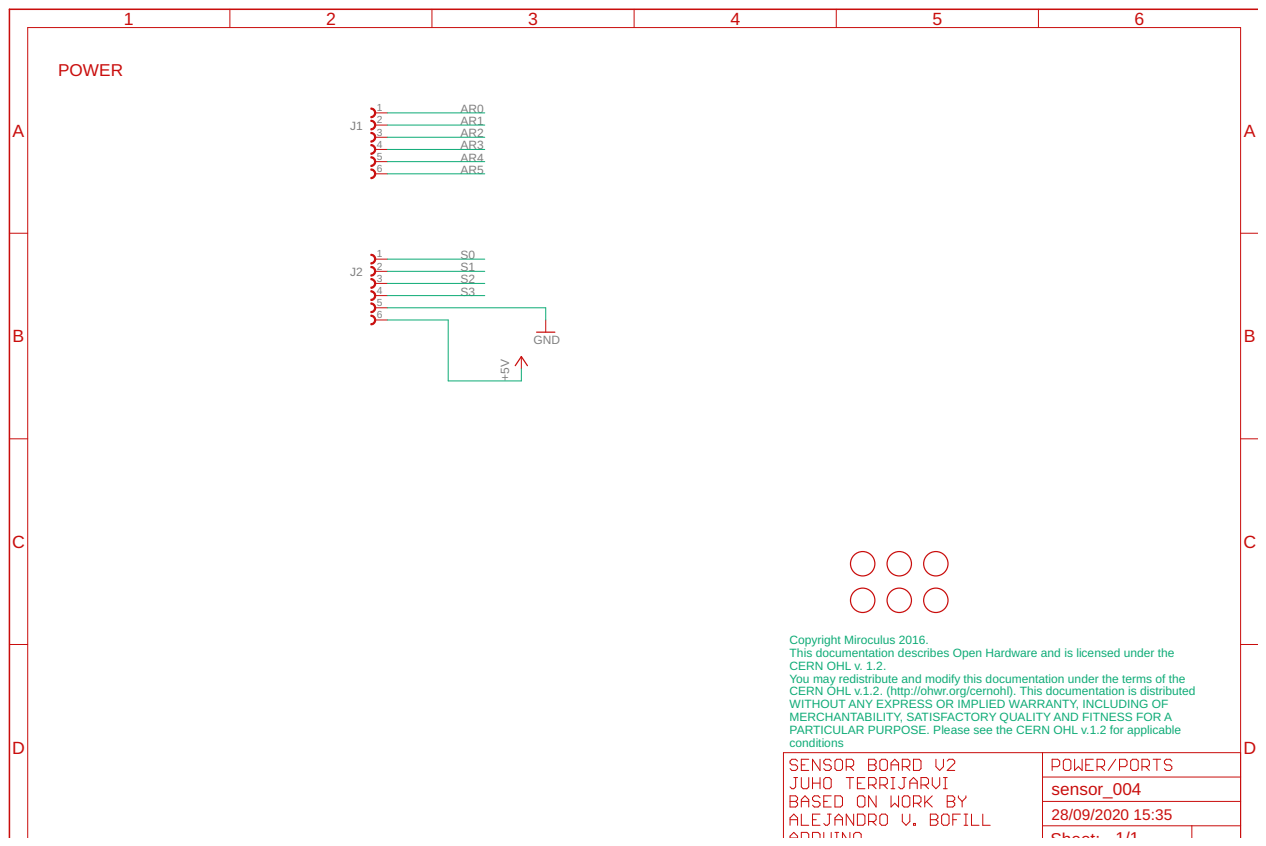
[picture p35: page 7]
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

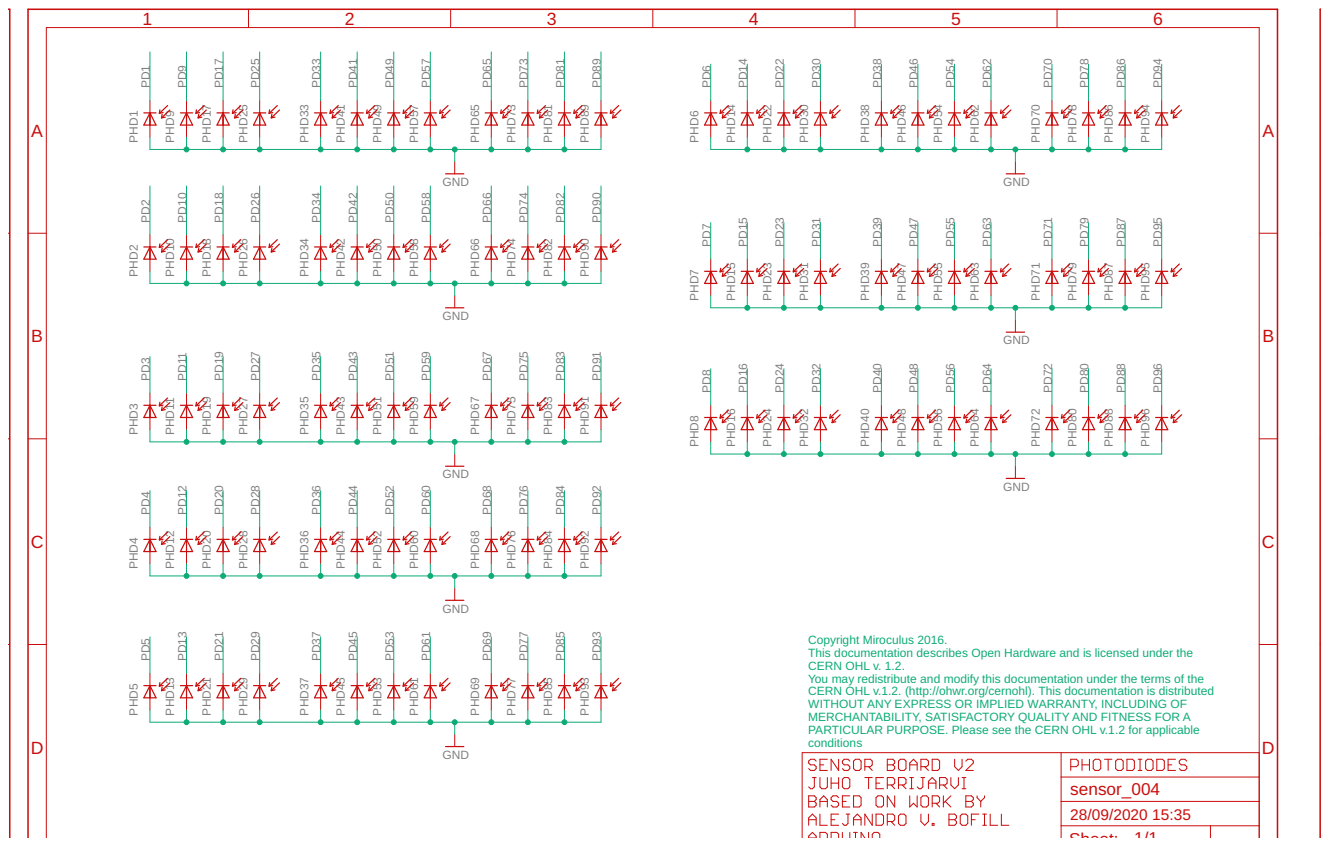
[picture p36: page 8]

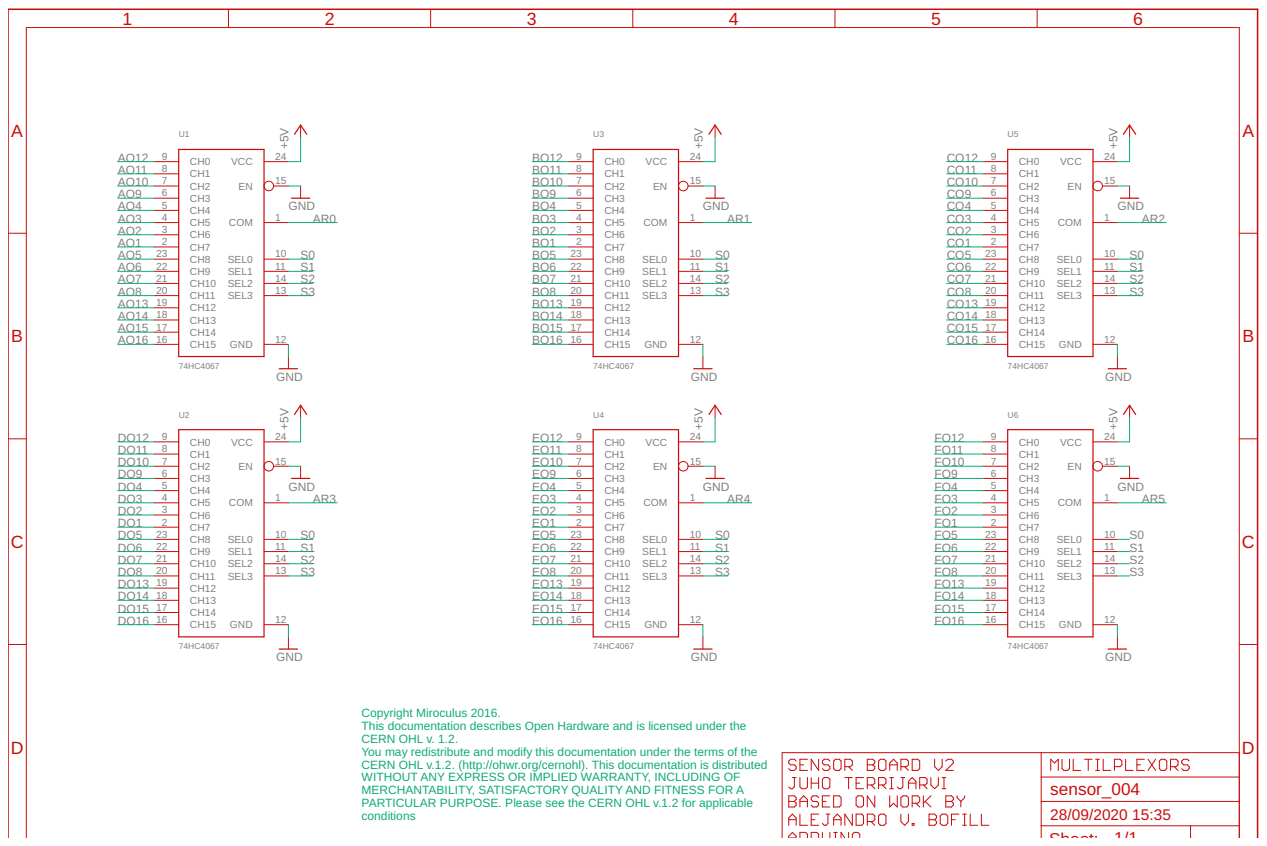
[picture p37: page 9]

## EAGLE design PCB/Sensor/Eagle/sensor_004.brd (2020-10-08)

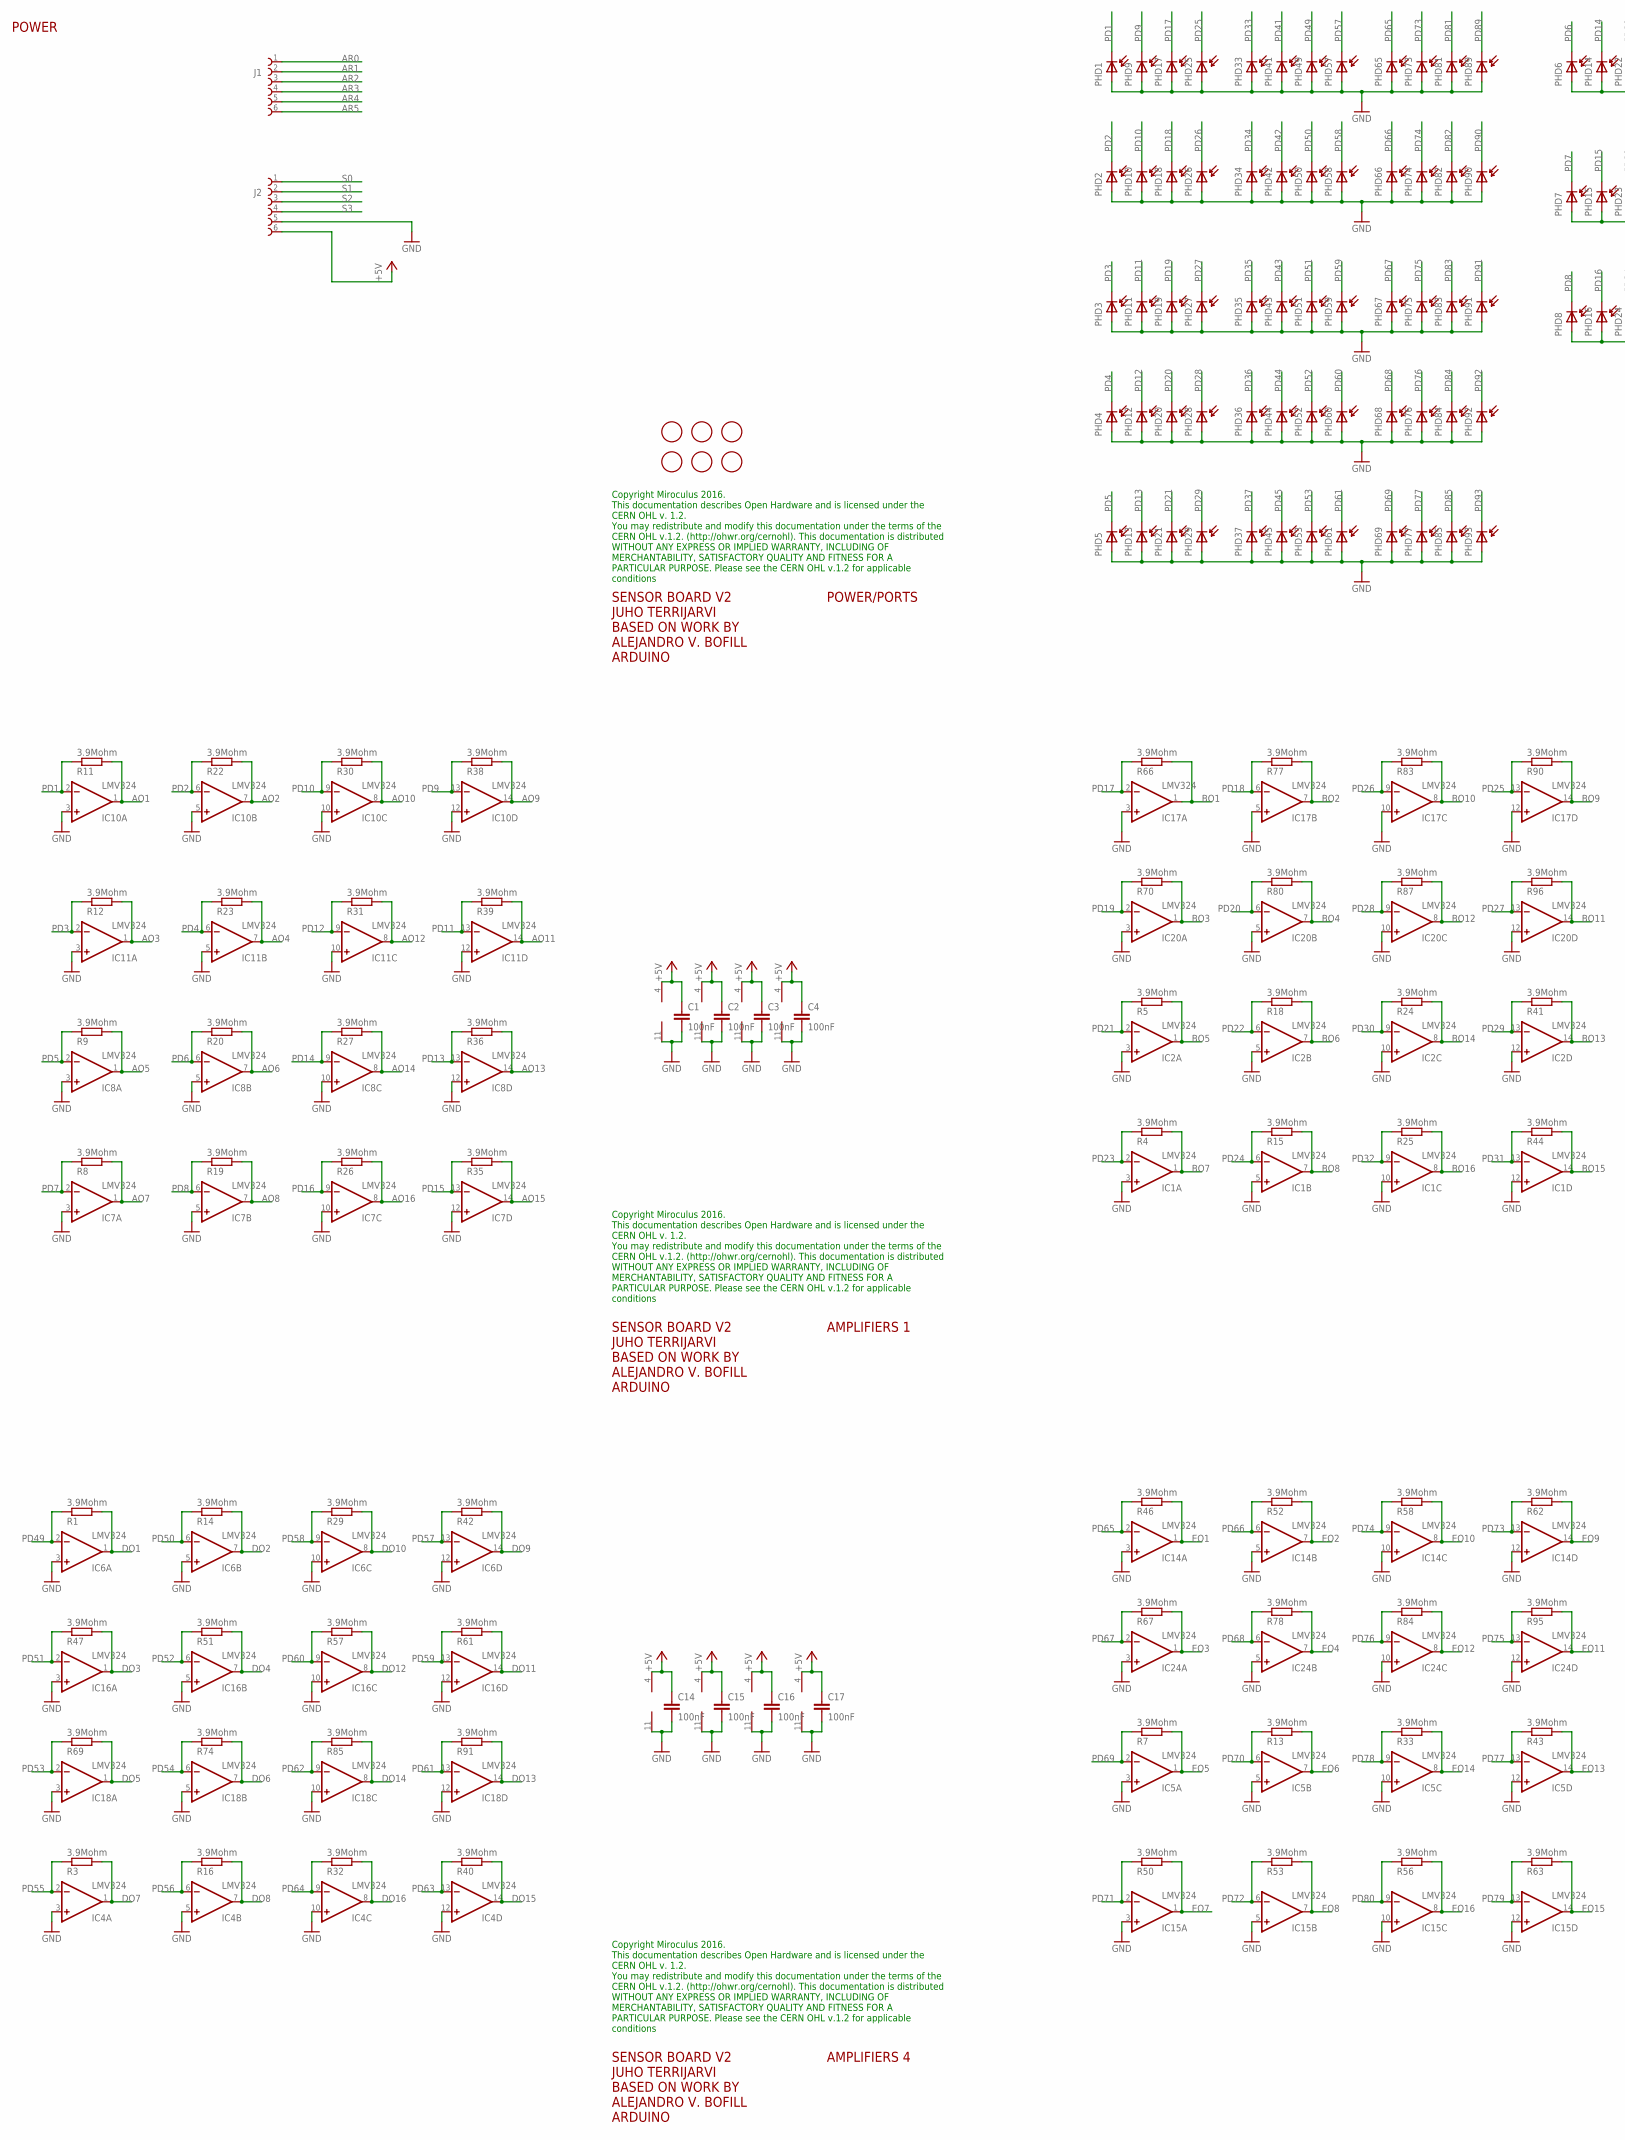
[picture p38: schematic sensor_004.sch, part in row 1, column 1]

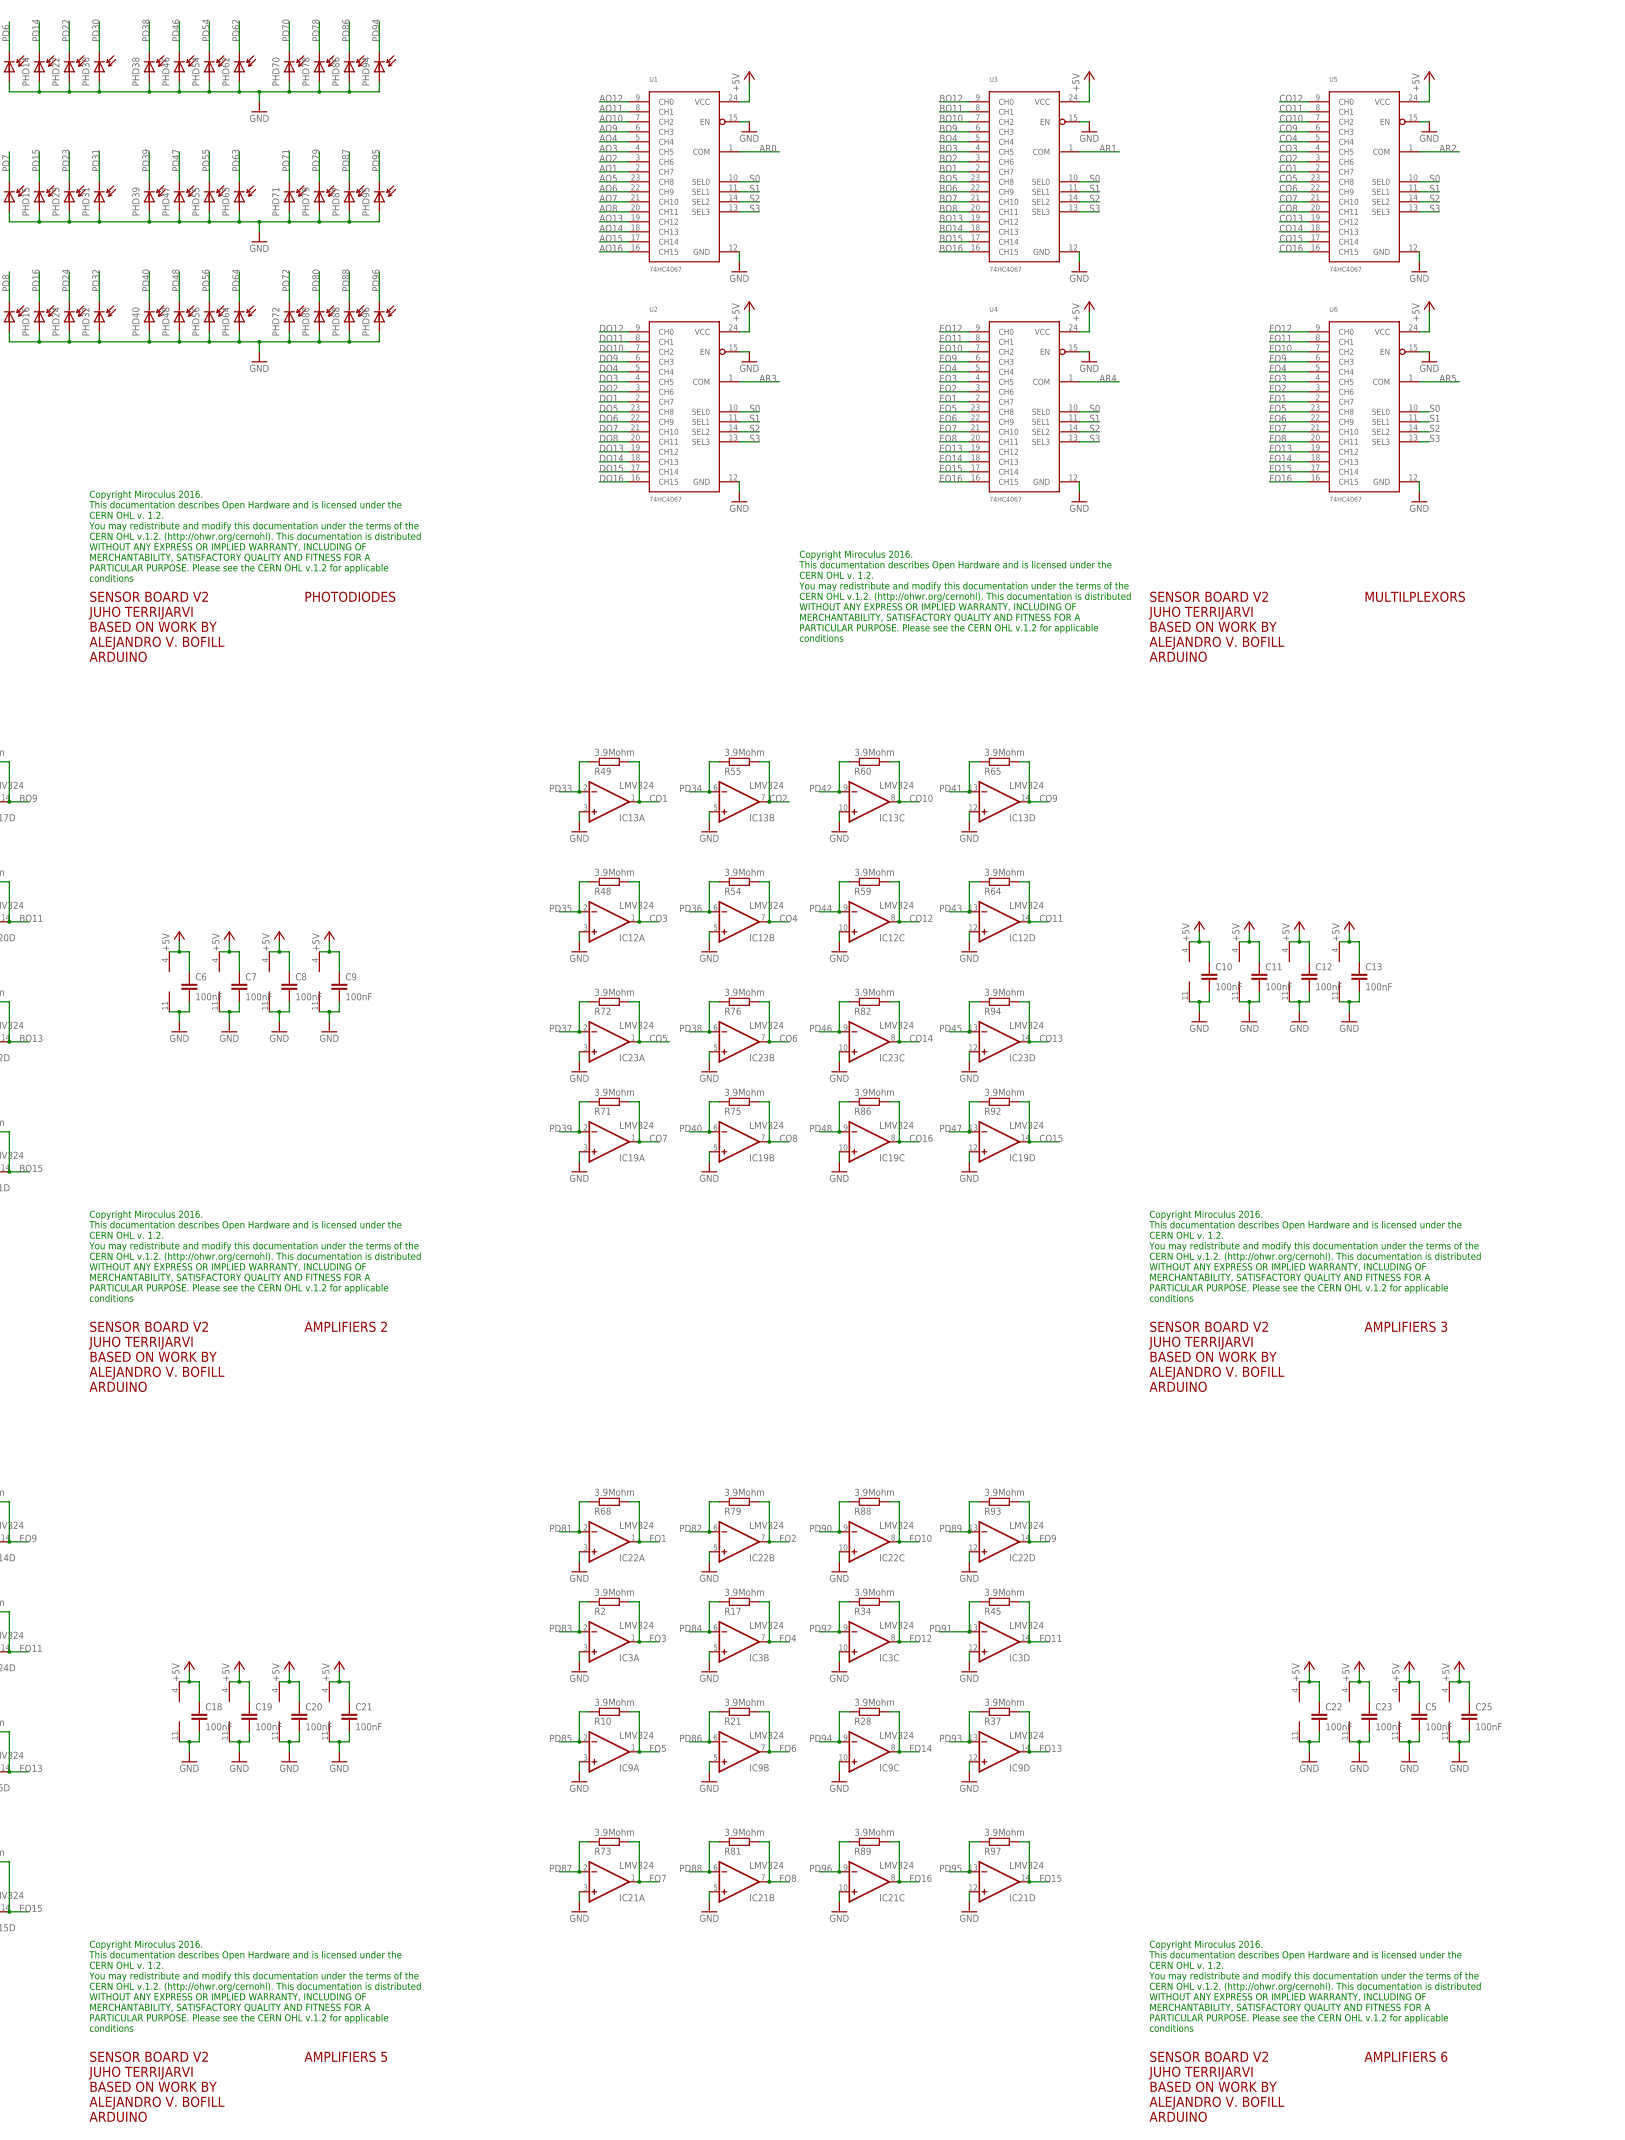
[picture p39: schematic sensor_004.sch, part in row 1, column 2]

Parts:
C1, C2, C3, C4, C5, C6, C7, C8, C9, C10, C11, C12, C13, C14, C15, C16, C17, C18, C19, C20, C21, C22, C23, C25: 100nF; C0603
FD1, FD2, FD3, FD4, FD5, FD6: FIDUCIALMOUNT; FIDUCIA-MOUNT
IC1, IC2, IC3, IC4, IC5, IC6, IC7, IC8, IC9, IC10, IC11, IC12, IC13, IC14, IC15, IC16, IC17, IC18, IC19, IC20, IC21, IC22, IC23, IC24: LMV324; SO14
J1, J2: 68710614522
PHD1, PHD2, PHD3, PHD4, PHD5, PHD6, PHD7, PHD8, PHD9, PHD10, PHD11, PHD12, PHD13, PHD14, PHD15, PHD16, PHD17, PHD18, PHD19, PHD20, PHD21, PHD22, PHD23, PHD24, PHD25, PHD26, PHD27, PHD28, PHD29, PHD30, PHD31, PHD32, PHD33, PHD34, PHD35, PHD36, PHD37, PHD38, PHD39, PHD40, PHD41, PHD42, PHD43, PHD44, PHD45, PHD46, PHD47, PHD48, PHD49, PHD50, PHD51, PHD52, PHD53, PHD54, PHD55, PHD56, PHD57, PHD58, PHD59, PHD60, PHD61, PHD62, PHD63, PHD64, PHD65, PHD66, PHD67, PHD68, PHD69, PHD70, PHD71, PHD72, PHD73, PHD74, PHD75, PHD76, PHD77, PHD78, PHD79, PHD80, PHD81, PHD82, PHD83, PHD84, PHD85, PHD86, PHD87, PHD88, PHD89, PHD90, PHD91, PHD92, PHD93, PHD94, PHD95, PHD96: CLS15-22C/L213G/TR8; PD_2
R1, R2, R3, R4, R5, R7, R8, R9, R10, R11, R12, R13, R14, R15, R16, R17, R18, R19, R20, R21, R22, R23, R24, R25, R26, R27, R28, R29, R30, R31, R32, R33, R34, R35, R36, R37, R38, R39, R40, R41, R42, R43, R44, R45, R46, R47, R48, R49, R50, R51, R52, R53, R54, R55, R56, R57, R58, R59, R60, R61, R62, R63, R64, R65, R66, R67, R68, R69, R70, R71, R72, R73, R74, R75, R76, R77, R78, R79, R80, R81, R82, R83, R84, R85, R86, R87, R88, R89, R90, R91, R92, R93, R94, R95, R96, R97: 3.9Mohm; R0603
U1, U2, U3, U4, U5, U6: 74HC4067; SSOP24

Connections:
+5V: C1.1, C2.1, C3.1, C4.1, C5.1, C6.1, C7.1, C8.1, C9.1, C10.1, C11.1, C12.1, C13.1, C14.1, C15.1, C16.1, C17.1, C18.1, C19.1, C20.1, C21.1, C22.1, C23.1, C25.1, IC1.4 (V+), IC2.4 (V+), IC3.4 (V+), IC4.4 (V+), IC5.4 (V+), IC6.4 (V+), IC7.4 (V+), IC8.4 (V+), IC9.4 (V+), IC10.4 (V+), IC11.4 (V+), IC12.4 (V+), IC13.4 (V+), IC14.4 (V+), IC15.4 (V+), IC16.4 (V+), IC17.4 (V+), IC18.4 (V+), IC19.4 (V+), IC20.4 (V+), IC21.4 (V+), IC22.4 (V+), IC23.4 (V+), IC24.4 (V+), J2.6, U1.24 (VCC), U2.24 (VCC), U3.24 (VCC), U4.24 (VCC), U5.24 (VCC), U6.24 (VCC)
AO1: IC10.1 (OUT), R11.2, U1.2 (CH7)
AO2: IC10.7 (OUT), R22.2, U1.3 (CH6)
AO3: IC11.1 (OUT), R12.2, U1.4 (CH5)
AO4: IC11.7 (OUT), R23.2, U1.5 (CH4)
AO5: IC8.1 (OUT), R9.2, U1.23 (CH8)
AO6: IC8.7 (OUT), R20.2, U1.22 (CH9)
AO7: IC7.1 (OUT), R8.2, U1.21 (CH10)
AO8: IC7.7 (OUT), R19.2, U1.20 (CH11)
AO9: IC10.14 (OUT), R38.2, U1.6 (CH3)
AO10: IC10.8 (OUT), R30.2, U1.7 (CH2)
AO11: IC11.14 (OUT), R39.2, U1.8 (CH1)
AO12: IC11.8 (OUT), R31.2, U1.9 (CH0)
AO13: IC8.14 (OUT), R36.2, U1.19 (CH12)
AO14: IC8.8 (OUT), R27.2, U1.18 (CH13)
AO15: IC7.14 (OUT), R35.2, U1.17 (CH14)
AO16: IC7.8 (OUT), R26.2, U1.16 (CH15)
AR0: J1.1, U1.1 (COM)
AR1: J1.2, U3.1 (COM)
AR2: J1.3, U5.1 (COM)
AR3: J1.4, U2.1 (COM)
AR4: J1.5, U4.1 (COM)
AR5: J1.6, U6.1 (COM)
BO1: IC17.1 (OUT), R66.2, U3.2 (CH7)
BO2: IC17.7 (OUT), R77.2, U3.3 (CH6)
BO3: IC20.1 (OUT), R70.2, U3.4 (CH5)
BO4: IC20.7 (OUT), R80.2, U3.5 (CH4)
BO5: IC2.1 (OUT), R5.2, U3.23 (CH8)
BO6: IC2.7 (OUT), R18.2, U3.22 (CH9)
BO7: IC1.1 (OUT), R4.2, U3.21 (CH10)
BO8: IC1.7 (OUT), R15.2, U3.20 (CH11)
BO9: IC17.14 (OUT), R90.2, U3.6 (CH3)
BO10: IC17.8 (OUT), R83.2, U3.7 (CH2)
BO11: IC20.14 (OUT), R96.2, U3.8 (CH1)
BO12: IC20.8 (OUT), R87.2, U3.9 (CH0)
BO13: IC2.14 (OUT), R41.2, U3.19 (CH12)
BO14: IC2.8 (OUT), R24.2, U3.18 (CH13)
BO15: IC1.14 (OUT), R44.2, U3.17 (CH14)
BO16: IC1.8 (OUT), R25.2, U3.16 (CH15)
CO1: IC13.1 (OUT), R49.2, U5.2 (CH7)
CO2: IC13.7 (OUT), R55.2, U5.3 (CH6)
CO3: IC12.1 (OUT), R48.2, U5.4 (CH5)
CO4: IC12.7 (OUT), R54.2, U5.5 (CH4)
CO5: IC23.1 (OUT), R72.2, U5.23 (CH8)
CO6: IC23.7 (OUT), R76.2, U5.22 (CH9)
CO7: IC19.1 (OUT), R71.2, U5.21 (CH10)
CO8: IC19.7 (OUT), R75.2, U5.20 (CH11)
CO9: IC13.14 (OUT), R65.2, U5.6 (CH3)
CO10: IC13.8 (OUT), R60.2, U5.7 (CH2)
CO11: IC12.14 (OUT), R64.2, U5.8 (CH1)
CO12: IC12.8 (OUT), R59.2, U5.9 (CH0)
CO13: IC23.14 (OUT), R94.2, U5.19 (CH12)
CO14: IC23.8 (OUT), R82.2, U5.18 (CH13)
CO15: IC19.14 (OUT), R92.2, U5.17 (CH14)
CO16: IC19.8 (OUT), R86.2, U5.16 (CH15)
DO1: IC6.1 (OUT), R1.2, U2.2 (CH7)
DO2: IC6.7 (OUT), R14.2, U2.3 (CH6)
DO3: IC16.1 (OUT), R47.2, U2.4 (CH5)
DO4: IC16.7 (OUT), R51.2, U2.5 (CH4)
DO5: IC18.1 (OUT), R69.2, U2.23 (CH8)
DO6: IC18.7 (OUT), R74.2, U2.22 (CH9)
DO7: IC4.1 (OUT), R3.2, U2.21 (CH10)
DO8: IC4.7 (OUT), R16.2, U2.20 (CH11)
DO9: IC6.14 (OUT), R42.2, U2.6 (CH3)
DO10: IC6.8 (OUT), R29.2, U2.7 (CH2)
DO11: IC16.14 (OUT), R61.2, U2.8 (CH1)
DO12: IC16.8 (OUT), R57.2, U2.9 (CH0)
DO13: IC18.14 (OUT), R91.2, U2.19 (CH12)
DO14: IC18.8 (OUT), R85.2, U2.18 (CH13)
DO15: IC4.14 (OUT), R40.2, U2.17 (CH14)
DO16: IC4.8 (OUT), R32.2, U2.16 (CH15)
EO1: IC14.1 (OUT), R46.2, U4.2 (CH7)
EO2: IC14.7 (OUT), R52.2, U4.3 (CH6)
EO3: IC24.1 (OUT), R67.2, U4.4 (CH5)
EO4: IC24.7 (OUT), R78.2, U4.5 (CH4)
EO5: IC5.1 (OUT), R7.2, U4.23 (CH8)
EO6: IC5.7 (OUT), R13.2, U4.22 (CH9)
EO7: IC15.1 (OUT), R50.2, U4.21 (CH10)
EO8: IC15.7 (OUT), R53.2, U4.20 (CH11)
EO9: IC14.14 (OUT), R62.2, U4.6 (CH3)
EO10: IC14.8 (OUT), R58.2, U4.7 (CH2)
EO11: IC24.14 (OUT), R95.2, U4.8 (CH1)
EO12: IC24.8 (OUT), R84.2, U4.9 (CH0)
EO13: IC5.14 (OUT), R43.2, U4.19 (CH12)
EO14: IC5.8 (OUT), R33.2, U4.18 (CH13)
EO15: IC15.14 (OUT), R63.2, U4.17 (CH14)
EO16: IC15.8 (OUT), R56.2, U4.16 (CH15)
FO1: IC22.1 (OUT), R68.2, U6.2 (CH7)
FO2: IC22.7 (OUT), R79.2, U6.3 (CH6)
FO3: IC3.1 (OUT), R2.2, U6.4 (CH5)
FO4: IC3.7 (OUT), R17.2, U6.5 (CH4)
FO5: IC9.1 (OUT), R10.2, U6.23 (CH8)
FO6: IC9.7 (OUT), R21.2, U6.22 (CH9)
FO7: IC21.1 (OUT), R73.2, U6.21 (CH10)
FO8: IC21.7 (OUT), R81.2, U6.20 (CH11)
FO9: IC22.14 (OUT), R93.2, U6.6 (CH3)
FO10: IC22.8 (OUT), R88.2, U6.7 (CH2)
FO11: IC3.14 (OUT), R45.2, U6.8 (CH1)
FO12: IC3.8 (OUT), R34.2, U6.9 (CH0)
FO13: IC9.14 (OUT), R37.2, U6.19 (CH12)
FO14: IC9.8 (OUT), R28.2, U6.18 (CH13)
FO15: IC21.14 (OUT), R97.2, U6.17 (CH14)
FO16: IC21.8 (OUT), R89.2, U6.16 (CH15)
GND: C1.2, C2.2, C3.2, C4.2, C5.2, C6.2, C7.2, C8.2, C9.2, C10.2, C11.2, C12.2, C13.2, C14.2, C15.2, C16.2, C17.2, C18.2, C19.2, C20.2, C21.2, C22.2, C23.2, C25.2, IC1.3 (+IN), IC1.5 (+IN), IC1.10 (+IN), IC1.11 (V-), IC1.12 (+IN), IC2.3 (+IN), IC2.5 (+IN), IC2.10 (+IN), IC2.11 (V-), IC2.12 (+IN), IC3.3 (+IN), IC3.5 (+IN), IC3.10 (+IN), IC3.11 (V-), IC3.12 (+IN), IC4.3 (+IN), IC4.5 (+IN), IC4.10 (+IN), IC4.11 (V-), IC4.12 (+IN), IC5.3 (+IN), IC5.5 (+IN), IC5.10 (+IN), IC5.11 (V-), IC5.12 (+IN), IC6.3 (+IN), IC6.5 (+IN), IC6.10 (+IN), IC6.11 (V-), IC6.12 (+IN), IC7.3 (+IN), IC7.5 (+IN), IC7.10 (+IN), IC7.11 (V-), IC7.12 (+IN), IC8.3 (+IN), IC8.5 (+IN), IC8.10 (+IN), IC8.11 (V-), IC8.12 (+IN), IC9.3 (+IN), IC9.5 (+IN), IC9.10 (+IN), IC9.11 (V-), IC9.12 (+IN), IC10.3 (+IN), IC10.5 (+IN), IC10.10 (+IN), IC10.11 (V-), IC10.12 (+IN), IC11.3 (+IN), IC11.5 (+IN), IC11.10 (+IN), IC11.11 (V-), IC11.12 (+IN), IC12.3 (+IN), IC12.5 (+IN), IC12.10 (+IN), IC12.11 (V-), IC12.12 (+IN), IC13.3 (+IN), IC13.5 (+IN), IC13.10 (+IN), IC13.11 (V-), IC13.12 (+IN), IC14.3 (+IN), IC14.5 (+IN), IC14.10 (+IN), IC14.11 (V-), IC14.12 (+IN), IC15.3 (+IN), IC15.5 (+IN), IC15.10 (+IN), IC15.11 (V-), IC15.12 (+IN), IC16.3 (+IN), IC16.5 (+IN), IC16.10 (+IN), IC16.11 (V-), IC16.12 (+IN), IC17.3 (+IN), IC17.5 (+IN), IC17.10 (+IN), IC17.11 (V-), IC17.12 (+IN), IC18.3 (+IN), IC18.5 (+IN), IC18.10 (+IN), IC18.11 (V-), IC18.12 (+IN), IC19.3 (+IN), IC19.5 (+IN), IC19.10 (+IN), IC19.11 (V-), IC19.12 (+IN), IC20.3 (+IN), IC20.5 (+IN), IC20.10 (+IN), IC20.11 (V-), IC20.12 (+IN), IC21.3 (+IN), IC21.5 (+IN), IC21.10 (+IN), IC21.11 (V-), IC21.12 (+IN), IC22.3 (+IN), IC22.5 (+IN), IC22.10 (+IN), IC22.11 (V-), IC22.12 (+IN), IC23.3 (+IN), IC23.5 (+IN), IC23.10 (+IN), IC23.11 (V-), IC23.12 (+IN), IC24.3 (+IN), IC24.5 (+IN), IC24.10 (+IN), IC24.11 (V-), IC24.12 (+IN), J2.5, PHD1.1, PHD2.1, PHD3.1, PHD4.1, PHD5.1, PHD6.1, PHD7.1, PHD8.1, PHD9.1, PHD10.1, PHD11.1, PHD12.1, PHD13.1, PHD14.1, PHD15.1, PHD16.1, PHD17.1, PHD18.1, PHD19.1, PHD20.1, PHD21.1, PHD22.1, PHD23.1, PHD24.1, PHD25.1, PHD26.1, PHD27.1, PHD28.1, PHD29.1, PHD30.1, PHD31.1, PHD32.1, PHD33.1, PHD34.1, PHD35.1, PHD36.1, PHD37.1, PHD38.1, PHD39.1, PHD40.1, PHD41.1, PHD42.1, PHD43.1, PHD44.1, PHD45.1, PHD46.1, PHD47.1, PHD48.1, PHD49.1, PHD50.1, PHD51.1, PHD52.1, PHD53.1, PHD54.1, PHD55.1, PHD56.1, PHD57.1, PHD58.1, PHD59.1, PHD60.1, PHD61.1, PHD62.1, PHD63.1, PHD64.1, PHD65.1, PHD66.1, PHD67.1, PHD68.1, PHD69.1, PHD70.1, PHD71.1, PHD72.1, PHD73.1, PHD74.1, PHD75.1, PHD76.1, PHD77.1, PHD78.1, PHD79.1, PHD80.1, PHD81.1, PHD82.1, PHD83.1, PHD84.1, PHD85.1, PHD86.1, PHD87.1, PHD88.1, PHD89.1, PHD90.1, PHD91.1, PHD92.1, PHD93.1, PHD94.1, PHD95.1, PHD96.1, U1.12 (GND), U1.15 (EN), U2.12 (GND), U2.15 (EN), U3.12 (GND), U3.15 (EN), U4.12 (GND), U4.15 (EN), U5.12 (GND), U5.15 (EN), U6.12 (GND), U6.15 (EN)
PD1: IC10.2 (-IN), PHD1.2, R11.1
PD2: IC10.6 (-IN), PHD2.2, R22.1
PD3: IC11.2 (-IN), PHD3.2, R12.1
PD4: IC11.6 (-IN), PHD4.2, R23.1
PD5: IC8.2 (-IN), PHD5.2, R9.1
PD6: IC8.6 (-IN), PHD6.2, R20.1
PD7: IC7.2 (-IN), PHD7.2, R8.1
PD8: IC7.6 (-IN), PHD8.2, R19.1
PD9: IC10.13 (-IN), PHD9.2, R38.1
PD10: IC10.9 (-IN), PHD10.2, R30.1
PD11: IC11.13 (-IN), PHD11.2, R39.1
PD12: IC11.9 (-IN), PHD12.2, R31.1
PD13: IC8.13 (-IN), PHD13.2, R36.1
PD14: IC8.9 (-IN), PHD14.2, R27.1
PD15: IC7.13 (-IN), PHD15.2, R35.1
PD16: IC7.9 (-IN), PHD16.2, R26.1
PD17: IC17.2 (-IN), PHD17.2, R66.1
PD18: IC17.6 (-IN), PHD18.2, R77.1
PD19: IC20.2 (-IN), PHD19.2, R70.1
PD20: IC20.6 (-IN), PHD20.2, R80.1
PD21: IC2.2 (-IN), PHD21.2, R5.1
PD22: IC2.6 (-IN), PHD22.2, R18.1
PD23: IC1.2 (-IN), PHD23.2, R4.1
PD24: IC1.6 (-IN), PHD24.2, R15.1
PD25: IC17.13 (-IN), PHD25.2, R90.1
PD26: IC17.9 (-IN), PHD26.2, R83.1
PD27: IC20.13 (-IN), PHD27.2, R96.1
PD28: IC20.9 (-IN), PHD28.2, R87.1
PD29: IC2.13 (-IN), PHD29.2, R41.1
PD30: IC2.9 (-IN), PHD30.2, R24.1
PD31: IC1.13 (-IN), PHD31.2, R44.1
PD32: IC1.9 (-IN), PHD32.2, R25.1
PD33: IC13.2 (-IN), PHD33.2, R49.1
PD34: IC13.6 (-IN), PHD34.2, R55.1
PD35: IC12.2 (-IN), PHD35.2, R48.1
PD36: IC12.6 (-IN), PHD36.2, R54.1
PD37: IC23.2 (-IN), PHD37.2, R72.1
PD38: IC23.6 (-IN), PHD38.2, R76.1
PD39: IC19.2 (-IN), PHD39.2, R71.1
PD40: IC19.6 (-IN), PHD40.2, R75.1
PD41: IC13.13 (-IN), PHD41.2, R65.1
PD42: IC13.9 (-IN), PHD42.2, R60.1
PD43: IC12.13 (-IN), PHD43.2, R64.1
PD44: IC12.9 (-IN), PHD44.2, R59.1
PD45: IC23.13 (-IN), PHD45.2, R94.1
PD46: IC23.9 (-IN), PHD46.2, R82.1
PD47: IC19.13 (-IN), PHD47.2, R92.1
PD48: IC19.9 (-IN), PHD48.2, R86.1
PD49: IC6.2 (-IN), PHD49.2, R1.1
PD50: IC6.6 (-IN), PHD50.2, R14.1
PD51: IC16.2 (-IN), PHD51.2, R47.1
PD52: IC16.6 (-IN), PHD52.2, R51.1
PD53: IC18.2 (-IN), PHD53.2, R69.1
PD54: IC18.6 (-IN), PHD54.2, R74.1
PD55: IC4.2 (-IN), PHD55.2, R3.1
PD56: IC4.6 (-IN), PHD56.2, R16.1
PD57: IC6.13 (-IN), PHD57.2, R42.1
PD58: IC6.9 (-IN), PHD58.2, R29.1
PD59: IC16.13 (-IN), PHD59.2, R61.1
PD60: IC16.9 (-IN), PHD60.2, R57.1
PD61: IC18.13 (-IN), PHD61.2, R91.1
PD62: IC18.9 (-IN), PHD62.2, R85.1
PD63: IC4.13 (-IN), PHD63.2, R40.1
PD64: IC4.9 (-IN), PHD64.2, R32.1
PD65: IC14.2 (-IN), PHD65.2, R46.1
PD66: IC14.6 (-IN), PHD66.2, R52.1
PD67: IC24.2 (-IN), PHD67.2, R67.1
PD68: IC24.6 (-IN), PHD68.2, R78.1
PD69: IC5.2 (-IN), PHD69.2, R7.1
PD70: IC5.6 (-IN), PHD70.2, R13.1
PD71: IC15.2 (-IN), PHD71.2, R50.1
PD72: IC15.6 (-IN), PHD72.2, R53.1
PD73: IC14.13 (-IN), PHD73.2, R62.1
PD74: IC14.9 (-IN), PHD74.2, R58.1
PD75: IC24.13 (-IN), PHD75.2, R95.1
PD76: IC24.9 (-IN), PHD76.2, R84.1
PD77: IC5.13 (-IN), PHD77.2, R43.1
PD78: IC5.9 (-IN), PHD78.2, R33.1
PD79: IC15.13 (-IN), PHD79.2, R63.1
PD80: IC15.9 (-IN), PHD80.2, R56.1
PD81: IC22.2 (-IN), PHD81.2, R68.1
PD82: IC22.6 (-IN), PHD82.2, R79.1
PD83: IC3.2 (-IN), PHD83.2, R2.1
PD84: IC3.6 (-IN), PHD84.2, R17.1
PD85: IC9.2 (-IN), PHD85.2, R10.1
PD86: IC9.6 (-IN), PHD86.2, R21.1
PD87: IC21.2 (-IN), PHD87.2, R73.1
PD88: IC21.6 (-IN), PHD88.2, R81.1
PD89: IC22.13 (-IN), PHD89.2, R93.1
PD90: IC22.9 (-IN), PHD90.2, R88.1
PD91: IC3.13 (-IN), PHD91.2, R45.1
PD92: IC3.9 (-IN), PHD92.2, R34.1
PD93: IC9.13 (-IN), PHD93.2, R37.1
PD94: IC9.9 (-IN), PHD94.2, R28.1
PD95: IC21.13 (-IN), PHD95.2, R97.1
PD96: IC21.9 (-IN), PHD96.2, R89.1
S0: J2.1, U1.10 (SEL0), U2.10 (SEL0), U3.10 (SEL0), U4.10 (SEL0), U5.10 (SEL0), U6.10 (SEL0)
S1: J2.2, U1.11 (SEL1), U2.11 (SEL1), U3.11 (SEL1), U4.11 (SEL1), U5.11 (SEL1), U6.11 (SEL1)
S2: J2.3, U1.14 (SEL2), U2.14 (SEL2), U3.14 (SEL2), U4.14 (SEL2), U5.14 (SEL2), U6.14 (SEL2)
S3: J2.4, U1.13 (SEL3), U2.13 (SEL3), U3.13 (SEL3), U4.13 (SEL3), U5.13 (SEL3), U6.13 (SEL3)

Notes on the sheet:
SENSOR BOARD V2 JUHO TERRIJARVI BASED ON WORK BY ALEJANDRO V. BOFILL ARDUINO
POWER
POWER/PORTS
PHOTODIODES
AMPLIFIERS 1
AMPLIFIERS 2
AMPLIFIERS 3
AMPLIFIERS 4
AMPLIFIERS 5
AMPLIFIERS 6
MULTILPLEXORS
Copyright Miroculus 2016. This documentation describes Open Hardware and is licensed under the CERN OHL v. 1.2. You may redistribute and modify this documentation under the terms of the CERN OHL v.1.2. (http://ohwr.org/cernohl). This documentation is distributed WITHOUT ANY EXPRESS OR IMPLIED WARRA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

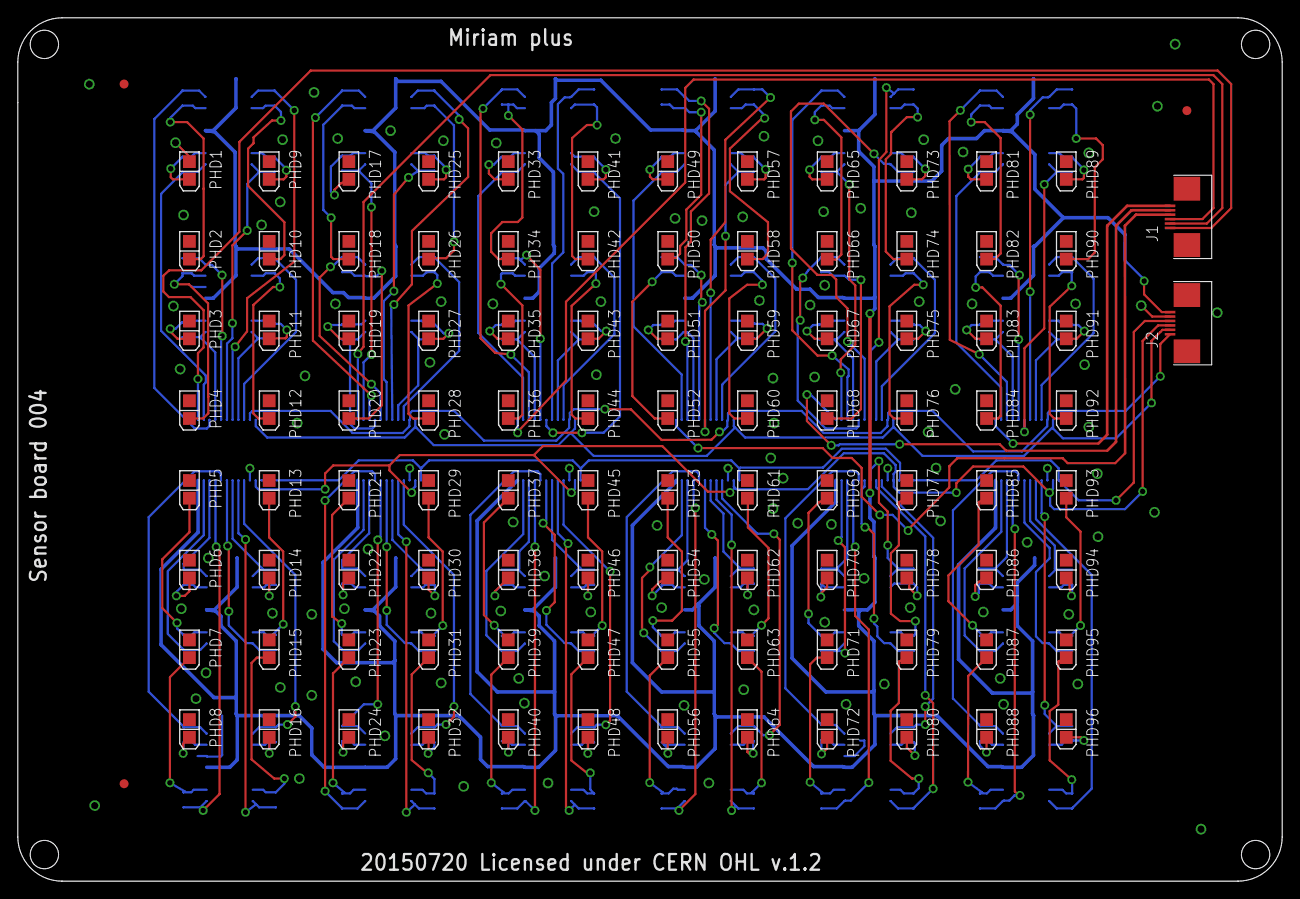
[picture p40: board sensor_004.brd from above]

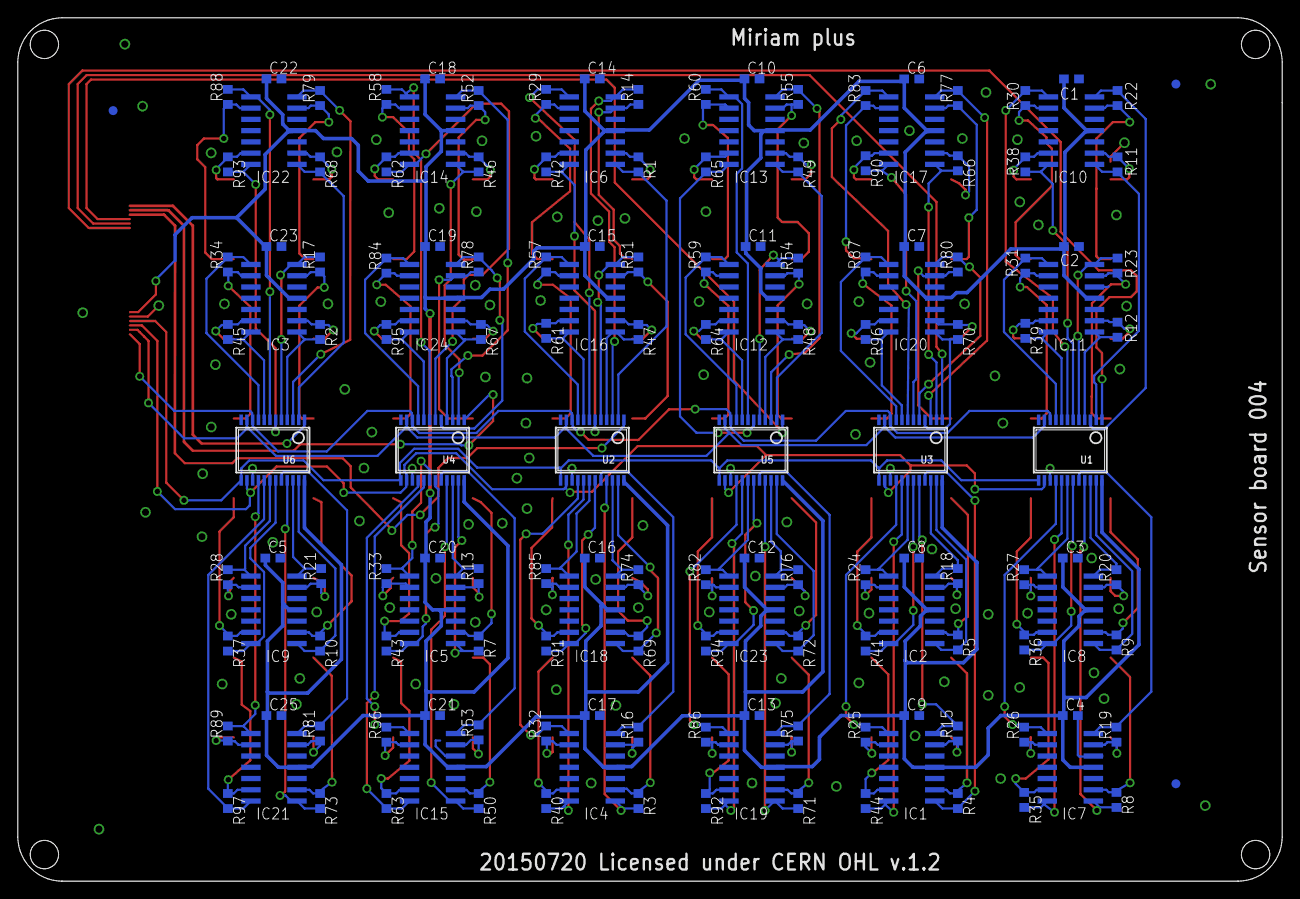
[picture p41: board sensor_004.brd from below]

Board: 2 copper layers, 142.8 x 97.5 mm, 254 parts (153 on the bottom side), 204 nets.

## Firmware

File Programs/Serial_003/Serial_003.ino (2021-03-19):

/*
 * Miriam control
 *
 * Miriam is an isothermal amplification unit capable of real time detection that supports a 96 well PCR plate
 * This firmware allows the control over serial port string messages
 *
 * The basic configuration of the board is:
 *
 * - Temperature Sensors pins: 23,24,25,26 and sensor 5 not using but connect to 19
 * - Heater pins: 9,10,1,13 and heat 5 not using but connect to 14
 * - LEDS: 22,2,12,11
 *
 * (c) 2016 Juho Terrijarvi juho@miroculus.com, Miroculus Inc.
 * (c) 2014 Juanjo Tara j.tara@arduino.cc, Arduino Verkstad AB
 *
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
 *  You should have received a copy of the GNU General Public License
 *  along with this program.  If not, see <http://www.gnu.org/licenses/>.
 */

#include <PID_v1.h>
#include <math.h>
#include "MyStatusLed.h"

#define FIRMWARE_VERSION "2.0.0" // first release 2.0.0

//Selector ping
#define SEL_1 46 // Selector ping 1
#define SEL_2 47 // Selector ping 2
#define SEL_3 48 // Selector ping 3
#define SEL_4 49 // Selector ping 4

//Temperature Sensors pin
#define TH_BOX A11        // Temperature Sensor 2
#define TH_MIDDLEBED_2 A9 // Temperature Sensor 3
#define TH_UPPERBED A10   // Temperature Sensor 1
#define TH_EXTRA A8       // Temperature Sensor ex

#define OPTIMAL_MIDDLE_TEMP 63
#define OPTIMAL_UPPER_TEMP 80
#define OPTIMAL_EXTRA_TEMP 63
#define IDDLE_MIDDLE_TEMP 30
#define IDDLE_UPPER_TEMP 20
//#define Threshold_temp 0.5
//Heater pins
#define HEAT_MIDDLE 2 // Heat 1
#define HEAT_UPPER 3  // Heat 2
#define HEAT_EXTRA 5  // Heat 3

//LED Sensors pin
#define PANEL_LED 22

//Speaker pin
#define SOUND 7
#define STATUS_LED_PIN 6

// manufacturer data for episco NCP18XH103F03RB 10k thermistor
// simply delete this if you don't need it
// or use this idea to define your own thermistors
#define NCP18XH103F03RB 3380.0f, 298.15f, 10000.0f // B,T0,R0

// temperature calculation correction - linear fit coefficients. Applied only for t in Celsius
#define LR_CORR_SLOPE 0.96    //0.8433
#define LR_CORR_INTERCEPT 2.6 //4.2213

// STATES FOR STATE MACHINE
#define INIT 'I'
#define CANCEL 'C'
#define HEAT_BOARDS 'H'
#define INFO 'i'
#define SET_TEMP_UPPER 'U'
#define SET_TEMP_MIDDLE 'M'
#define SET_TEMP_EXTRA 'E'
#define READ_ASSAY 'R'
#define PLAY_SOUND 's'
#define STATUS_LED_ON 'l'
#define STATUS_LED_OFF 'o'
#define SET_BOX_THR 'T'
#define MELT_HEAT 'W'
#define MELT_INIT 'w'
#define VERSION 'V'

int MUL[6] = {
    A0, A1, A2, A3, A4, A5}; // These are the 6 analog inputs. One per multiplexer.

byte controlLPins[] = {
    B00000000,
    B00000001,
    B00000010,
    B00000011,
    B00000100,
    B00000101,
    B00000110,
    B00000111,
    B00001000,
    B00001001,
    B00001010,
    B00001011,
    B00001100,
    B00001101,
    B00001110,
    B00001111};

// Holds incoming values from Multiplexer. This is our 96 well plate.
int sensorValues[8][12] = {};

//Define the aggressive and conservative Tuning Parameters
double aggKp = 4, aggKi = 0.4, aggKd = 4;        // d2
double consKp = 1, consKi = 0.05, consKd = 0.25; //1, 0.25
double Setpoint;
//Define Variables we'll be connecting to PID's
double Input_MIDDLE, Output_MIDDLE, Setpoint_MIDDLE, Input_UPPER, Input_BOX, Setpoint_UPPER, Output_UPPER, Input_MIDDLE_2, Input_EXTRA, Output_EXTRA, Setpoint_EXTRA;
double threshold_BOX = 60;

//PID Controller for Heater
PID PID_MIDDLE(&Input_MIDDLE_2, &Output_MIDDLE, &Setpoint_MIDDLE, consKp, consKi, consKd, DIRECT);
PID PID_UPPER(&Input_UPPER, &Output_UPPER, &Setpoint_UPPER, consKp, consKi, consKd, DIRECT);
PID PID_EXTRA(&Input_EXTRA, &Output_EXTRA, &Setpoint_EXTRA, consKp, consKi, consKd, DIRECT);

// enumerating 3 major temperature scales
enum
{
  T_KELVIN = 0,
  T_CELSIUS,
  T_FAHRENHEIT
};

byte states[] = {
    INIT, CANCEL, HEAT_BOARDS, INFO, SET_TEMP_UPPER, SET_TEMP_MIDDLE, SET_TEMP_EXTRA, READ_ASSAY, PLAY_SOUND, STATUS_LED_ON, STATUS_LED_OFF, SET_BOX_THR, MELT_HEAT, MELT_INIT, VERSION};

// serial data
String inputString = "                         "; // a string to hold incoming data
String parameters = "                         ";
String dataString = "                         ";
boolean stringComplete = false; // whether the string is complete
boolean LED = false;
boolean HEAT_ON = false;
boolean MELT_ON = false;

int state = INIT;
char previous_state = INIT;
int defaultState = INIT;

bool heat_alarm = false;
//bool status_led_state_on=false;
//bool status_led_busy=false;

MyStatusLed status_led(STATUS_LED_PIN, 500, 500);

void setup()
{
  DDRL = DDRL | B00001111; // this sets pins D3 to D7 as outputs

  // Temperature Sensors pin
  pinMode(TH_BOX, INPUT);
  pinMode(TH_MIDDLEBED_2, INPUT);
  pinMode(TH_UPPERBED, INPUT);
  pinMode(TH_EXTRA, INPUT);

  // Heater pins
  pinMode(HEAT_MIDDLE, OUTPUT);
  pinMode(HEAT_UPPER, OUTPUT);
  pinMode(HEAT_EXTRA, OUTPUT);
  //Panel LEDS
  pinMode(PANEL_LED, OUTPUT);
  //  pinMode(STATUS_LED,OUTPUT);

  // Read temperature sensors
  ReaderSensorTemp();

  // Set degrees for PID algorithm
  Setpoint_MIDDLE = OPTIMAL_MIDDLE_TEMP;
  Setpoint_UPPER = OPTIMAL_UPPER_TEMP;
  Setpoint_EXTRA = OPTIMAL_EXTRA_TEMP;
  // input string needs space
  inputString.reserve(30);
  inputString = "";
  parameters = "";

  Serial.begin(9600); // Begin the serial monitor at 9600bps
  Serial.println(F("Hope your day is nice and shiny!"));
}

void loop()
{

  // print the string when a newline arrives:
  if (stringComplete)
  {
    // remove carriage returns and new lines
    inputString.replace("\n", "");
    inputString.replace("\r", "");
    Serial.println(inputString);

    // it there is anything to do with it, do it!
    if (isState(inputString[0]))
    {
      previous_state = state;
      state = inputString[0];
      parameters = inputString.substring(2);
    }
    // clear the string:

    inputString = "";
    stringComplete = false;
  }

  //Calculate PID for heaters
  if (HEAT_ON)
    Calculate_Heat();
  if (MELT_ON)
    Calculate_Melt();
  //Calculate_Heat();
  status_led.Update();

  //  if (status_led_on)

  // state machine
  switch (state)
  {

  case INIT:
    previous_state = state;
    state = 'I';
    break;

  case MELT_INIT:

    HEAT_ON = false;
    MELT_ON = false;

    Output_MIDDLE = 100;
    Output_UPPER = 100;
    Output_EXTRA = 100;
    computePIDs();

    Serial.println(F("INIT MELT$"));

    //turn the PID's off
    //     PID_MIDDLE.SetMode(MANUAL);
    //     PID_UPPER.SetMode(MANUAL);
    //     PID_EXTRA.SetMode(MANUAL);

    state = defaultState;
    break;

  case CANCEL:

    HEAT_ON = false;
    MELT_ON = false;

    Output_MIDDLE = 0;
    Output_UPPER = 0;
    Output_EXTRA = 0;

    Serial.println(F("Cancel$"));
    //delay(4000);

    //turn the PID's off
    PID_MIDDLE.SetMode(MANUAL);
    PID_UPPER.SetMode(MANUAL);
    PID_EXTRA.SetMode(MANUAL);

    //Setpoint_MIDDLE = IDDLE_MIDDLE_TEMP;
    //Setpoint_UPPER = IDDLE_UPPER_TEMP;

    status_led.SwitchMode(LED_OFF);

    state = defaultState;

    break;

  case HEAT_BOARDS:

    HEAT_ON = true;
    heat_alarm = true;
    status_led.SwitchMode(LED_BLINK);

    Serial.println(F("HEATING BOARDS$"));

    //turn the PID's on
    PID_MIDDLE.SetMode(AUTOMATIC);
    PID_UPPER.SetMode(AUTOMATIC);
    PID_EXTRA.SetMode(AUTOMATIC);
    state = defaultState;
    break;

  case MELT_HEAT:
    MELT_ON = true;
    //    heat_alarm = true;
    heat_alarm = false;

    Serial.println(F("MELTING BOARDS$"));

    //turn the PID's on
    PID_MIDDLE.SetMode(AUTOMATIC);
    PID_UPPER.SetMode(AUTOMATIC);
    PID_EXTRA.SetMode(AUTOMATIC);
    state = defaultState;
    break;

  case VERSION:
    //    Serial.print(F("firmware_version: "));
    Serial.print(FIRMWARE_VERSION);
    Serial.println("$");
    state = defaultState;
    break;

  case INFO:

    Serial.println(String(Output_MIDDLE) + "," + String(Output_UPPER) + "," +
                   String(analogRead(TH_UPPERBED)) + "," + String((analogRead(TH_MIDDLEBED_2))) + "," +
                   String(Temperature(TH_UPPERBED, T_CELSIUS, NCP18XH103F03RB, 10000.0f)) + "," +
                   String(Temperature(TH_MIDDLEBED_2, T_CELSIUS, NCP18XH103F03RB, 10000.0f)) + "," +
                   String(Output_EXTRA) + "," +
                   String((analogRead(TH_EXTRA))) + "," + String((analogRead(TH_BOX))) + "," +
                   //      String(Temperature(TH_EXTRA,T_CELSIUS,NCP18XH103F03RB,10000.0f)) + "," +
                   String(Temperature(TH_EXTRA, T_CELSIUS, NCP18XH103F03RB, 10000.0f)) + "," +
                   String(Temperature(TH_BOX, T_CELSIUS, NCP18XH103F03RB, 10000.0f)) + "$");

    // 0: output_M,
    // 1: output_U
    // 2: T_U
    // 3: T_M
    // 4: T_U_C
    // 5: T_M_C
    // 6: output_E
    // 7: T_E
    // 8: T_Box
    // 9: T_E_C
    // 10: T_Box_C

    state = defaultState;

    break;

  case SET_TEMP_UPPER:

    Setpoint_UPPER = parameters.toFloat();
    Serial.print(F("NEW UPPER TEMP:"));
    Serial.print(Setpoint_UPPER);
    Serial.println("$");

    state = defaultState;
    break;

  case SET_TEMP_MIDDLE:

    Setpoint_MIDDLE = parameters.toFloat();
    Serial.print(F("NEW MIDDLE TEMP:"));
    Serial.print(Setpoint_MIDDLE);
    Serial.println("$");

    state = defaultState;

    break;

  case SET_TEMP_EXTRA:
    Setpoint_EXTRA = parameters.toFloat();
    Serial.print(F("NEW EXTRA TEMP:"));
    Serial.print(Setpoint_EXTRA);
    Serial.println("$");

    state = defaultState;

    break;

  case READ_ASSAY:

    Serial.print(F("READ ASSAY"));
    Read_Assay();
    state = defaultState;

    // Read_Assay calls display_data() which eventually prints "$\n"
    break;

  case PLAY_SOUND:
    play_sound();
    state = defaultState;
    Serial.println(F("$"));
    break;

  case STATUS_LED_ON:

    status_led.SwitchMode(LED_ON);
    Serial.println(F("Status LED on$"));

    state = defaultState;
    break;

  case STATUS_LED_OFF:

    status_led.SwitchMode(LED_OFF);
    Serial.println(F("Status LED off$"));

    state = defaultState;
    break;

  case SET_BOX_THR:

    threshold_BOX = parameters.toFloat();
    Serial.print(F("NEW TEMP THRESHOLD:"));
    Serial.print(threshold_BOX);
    Serial.println("$");

    state = defaultState;
    break;
  }
}

void play_sound()
{

  tone(SOUND, 3000, 5000);
  delay(1000);
  tone(SOUND, 1000, 5000);
  delay(1000);
  tone(SOUND, 2000, 5000);
  delay(1000);
  tone(SOUND, 500, 5000);
  delay(1000);
  noTone(SOUND);
  delay(1000);
  //tone(piezoPin, 1000, 500);
  //delay(1000);
}

void setPin(int outputPin)
{
  // This selects the multiplexer state on all multiplexers. Since we use the
  // multiplexer only for reading the sensors, this picks the input to the
  // multiplexer from channel 0 through channel 15 (inclusive) to be output on
  // the output pin of the multiplexer.
  PORTL = controlLPins[outputPin];
}
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

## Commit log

2020-08-30 sensor2 wiring and FR4 heaters
2020-10-01 change sensor board and case
    [.cells.tsv, arduino_cover.stl, base.stl, body.stl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]
2020-10-01 add heat distribution
2020-10-08 beutify plot
    Yellow color replaced by Chocolate; the figure panel is resized with the form
    [mycells.tsv]
2020-10-08 remove unnecessary file
    [mycells.tsv]
2020-10-15 add heat uniformity
2020-10-15 add heat_simulation
2020-10-22 added new arduino file
2020-10-22 cancel heating on exit
2020-10-23 ino:changed the temperature readout formula for A11 (TH_EXTRA)
2020-10-23 reading temperatures with dicts, refactor arduino commands
2020-10-23 changed design for additional sensors; more refactoring for arduino readouts
2020-10-30 (ino) changed linear correction in temperature calculation
2020-11-02 serial005.ino: with sound alarm and status LED (not finished)
2020-11-04 ino: editable box temperature threshold
2020-11-06 RT-LAMP with Miriam flow
2020-11-06 Add assembly guide and new box
    [arduino_cover.stl, body.stl, box.stl, cap.stl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]
2020-11-09 update BOM list
    [LED_005.xlsx, LH_010.xlsx, Others.xlsx, SHIELD_008.xlsx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]
2020-11-13 fix heat canceling
2020-11-13 added box temperature threshold setting
2020-11-19 change calibration function of the thermistor
2020-11-25 make arduino PID_v1 library comply with spec
    See https://arduino.github.io/arduino-cli/latest/library-specification/
2020-11-25 update BOM
    [Others.xlsx]
2020-11-25 add continuous integration using github actions
    So far, this builds the Windows program and the Arduino firmware.
2020-12-11 fix temperature threshold check
2021-01-12 debug arduino artifact building
2021-01-19 ino: float input of temperature settings
2021-02-09 package arduino source with .exe
2021-02-26 perform ADC reads 500 microseconds after LED on
    We measured with an oscilloscope that the voltage coming into the analog
    input of the arduino rises over about 250 microseconds to a plateau.
    This should ensure that we are measuring the plateau level.
2021-03-08 update lockbar
    [lock_bar_new.stl]
2021-03-13 bugfix: turn off heaters in CANCEL
    This fixes #10.
2021-07-15 Correct a URL in shield 008 BOM
    [SHIELD_008.xlsx]
2021-07-15 Put sensor gerbers into gerber folder
    [copper_bottom.gbr, copper_top.gbr, drill_1_16.xln, gerber_job.gbrjob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]
2021-07-15 Make BOMs parse-able by Kitspace
    [LED_005.xlsx, LH_010.xlsx, Others.xlsx, SHIELD_008.xlsx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]

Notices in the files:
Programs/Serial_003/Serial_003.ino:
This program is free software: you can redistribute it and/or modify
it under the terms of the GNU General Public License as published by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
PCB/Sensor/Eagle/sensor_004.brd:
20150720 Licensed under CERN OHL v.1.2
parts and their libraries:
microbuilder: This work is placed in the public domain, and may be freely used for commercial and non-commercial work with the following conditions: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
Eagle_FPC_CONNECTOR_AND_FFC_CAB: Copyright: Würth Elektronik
